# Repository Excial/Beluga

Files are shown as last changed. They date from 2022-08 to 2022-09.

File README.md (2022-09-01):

# Beluga
1. Created a sensor board for Beluga robotics platform
2. Contains PCB, Arduino Code

## Project description
A biosensor designed for microbial auditing, which is mounted onboard an autonomous robot as a payload. The PCB in this sensor helps to initiate helps to reduce the streamline the electronics due to space constraints to initiate the sampling sequence / processes of the biosensor.

## Design Objectives
Practice Design objectives in accordance to the IPC-2221 Standard

### V1
[✓] 3.3V LDO

[✓] 12V Buck Converter

[✓] ESP32 Module 

[✓] Bootloader

[✓] Troubleshooting LEDs

[X] Motor Driver LEDs

  - Too bright, need to increase resistance from 1K to 10K.

[✓] Motor Drivers

[X] Circuit Protection

  - Circuit Protection LED mounted wrongly, refer to schematic.
  - Source and Drain of Mosfet is mounted wrongly, needs to be switched.

[✓] M2 Mounting holes

#### Improvements
1. Add a stepper Motor driver
2. Add a buzzer
3. Add a USB Port
4. Add a FDTI chip
5. Increase Resistance for LEDs from 1k to 10K
	5a. Might Remove the LEDs altogether

### V2

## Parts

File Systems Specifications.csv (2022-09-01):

Name | id | Component_class | current | voltage | capacitance | inductance
ESP32 | C701342 | Microcontroller | 0.3A | 3.3V | - | - | -
A3909 | C2653462 | Motor Driver | 0.3A | 12V | - | - | SSOP-10
LED1,LED2,LED3 | C72043 | LED Diode | 0.02A | 3.3V | - | - | 0603
R81 | C14675 | Resistor | - | - | - | - | 0603
C3,C4,C5 | C92487 | Capacitor | - | 16V | 10uF | - | 0603
I1 | C2929502 | Inductor | 60V | 3A | - | 33uH | 12.3x12.3x3.8mm

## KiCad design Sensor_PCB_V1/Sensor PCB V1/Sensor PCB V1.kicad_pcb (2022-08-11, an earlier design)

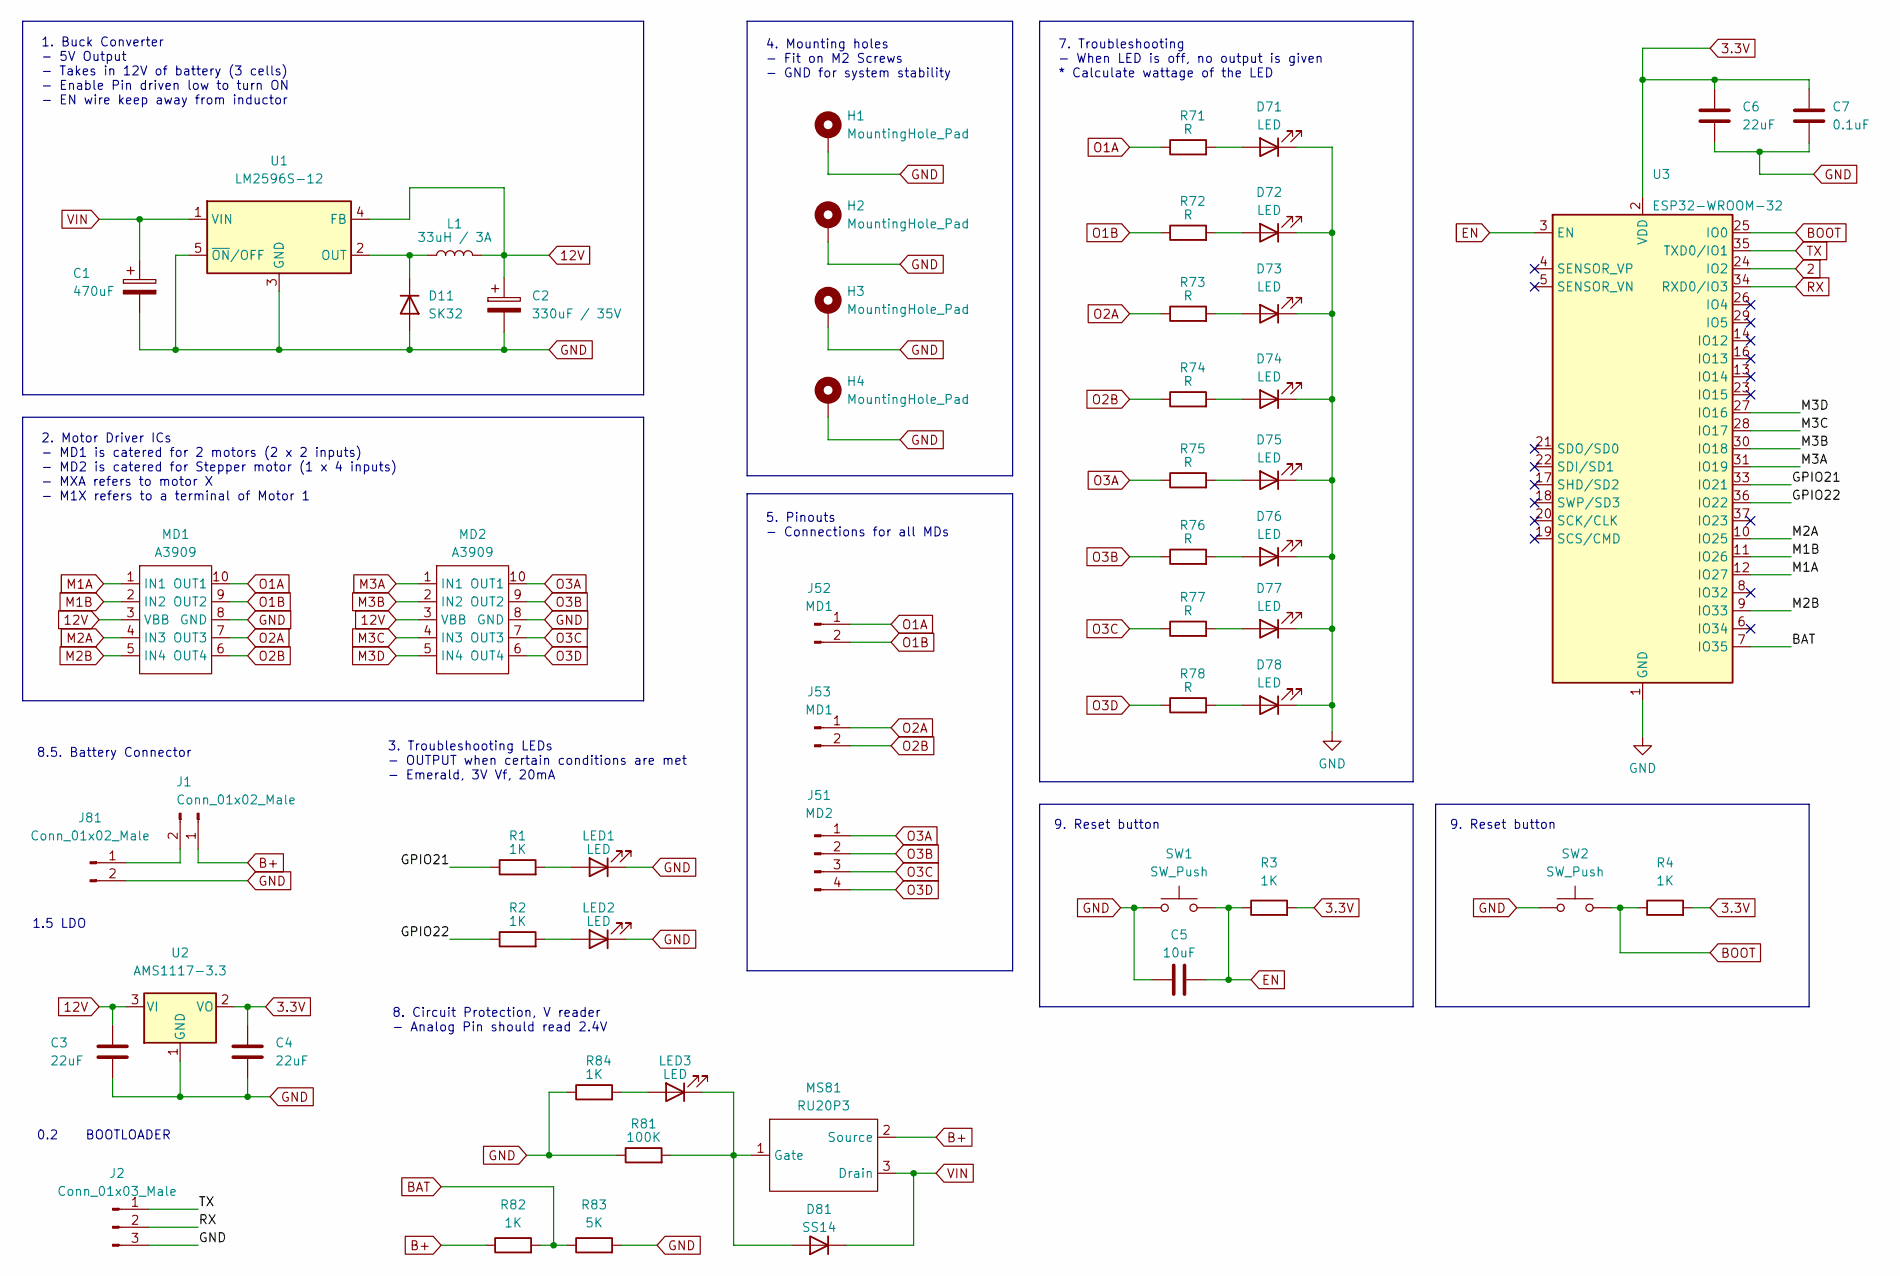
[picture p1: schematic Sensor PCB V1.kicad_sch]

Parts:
C1: 470uF; C_Elec_10x10.2
C2: 330uF / 35V; C_Elec_10x10.2
C3, C4, C6: 22uF; C_0603_1608Metric
C5: 10uF; C_0603_1608Metric
C7: 0.1uF; C_0603_1608Metric
D11: SK32; D_SOD-123F
D71, D72, D73, D74, D75, D76, D77, D78: LED; LED_0603_1608Metric
D81: SS14; D_SMA
H1, H2, H3, H4: MountingHole_Pad; MountingHole_2.2mm_M2_DIN965_Pad
J1, J81: Conn_01x02_Male; PinSocket_1x02_P2.54mm_Vertical
J2: Conn_01x03_Male; PinSocket_1x03_P2.54mm_Vertical
J51: MD2; PinSocket_1x04_P2.54mm_Vertical
J52, J53: MD1; PinSocket_1x02_P2.54mm_Vertical
L1: 33uH / 3A; L_12x12mm_H8mm
LED1, LED2, LED3: LED; LED_0603_1608Metric
MD1, MD2: A3909; SSOP-10_3.9x4.9mm_P1.00mm
MS81: RU20P3; SOT-23
R1, R2, R3, R4, R82, R84: 1K; R_0603_1608Metric
R71, R72, R73, R74, R75, R76, R77, R78: R; R_0603_1608Metric
R81: 100K; R_0603_1608Metric
R83: 5K; R_0603_1608Metric
SW1, SW2: SW_Push; SW_SPST_Omron_B3FS-100xP
U1: LM2596S-12; TO-263-5_TabPin3
U2: AMS1117-3.3; SOT-223-3_TabPin2
U3: ESP32-WROOM-32

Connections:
2: U3.24 (IO2)
3.3V: C4.1, C6.1, C7.1, R3.2, R4.2, U2.2 (VO), U3.2 (VDD)
12V: C2.1, C3.1, L1.2, MD1.3 (VBB), MD2.3 (VBB), U1.4 (FB), U2.3 (VI)
/GPIO21: R1.1, U3.33 (IO21)
/GPIO22: R2.1, U3.36 (IO22)
B+: J1.1, MS81.2 (Source), R82.1
BAT: R82.2, R83.1, U3.7 (IO35)
BOOT: R4.1, SW2.2, U3.25 (IO0)
EN: C5.2, R3.1, SW1.2, U3.3 (EN)
GND: C1.2, C2.2, C3.2, C4.2, C5.1, C6.2, C7.2, D11.2 (A), D71.1 (K), D72.1 (K), D73.1 (K), D74.1 (K), D75.1 (K), D76.1 (K), D77.1 (K), D78.1 (K), H1.1, H2.1, H3.1, H4.1, J2.3, J81.2, LED1.1 (K), LED2.1 (K), MD1.8 (GND), MD2.8 (GND), R81.1, R83.2, R84.1, SW1.1, SW2.1, U1.3 (GND), U1.5 (~ON/OFF), U2.1 (GND), U3.1 (GND), U3.15 (GND), U3.38 (GND), U3.39 (GND)
M1A: MD1.1 (IN1), U3.12 (IO27)
M1B: MD1.2 (IN2), U3.11 (IO26)
M2A: MD1.4 (IN3), U3.10 (IO25)
M2B: MD1.5 (IN4), U3.9 (IO33)
M3A: MD2.1 (IN1), U3.31 (IO19)
M3B: MD2.2 (IN2), U3.30 (IO18)
M3C: MD2.4 (IN3), U3.28 (IO17)
M3D: MD2.5 (IN4), U3.27 (IO16)
unnamed: D11.1 (K), L1.1, U1.2 (OUT)
unnamed: D71.2 (A), R71.2
unnamed: D72.2 (A), R72.2
unnamed: D73.2 (A), R73.2
unnamed: D74.2 (A), R74.2
unnamed: D75.2 (A), R75.2
unnamed: D76.2 (A), R76.2
unnamed: D77.2 (A), R77.2
unnamed: D78.2 (A), R78.2
unnamed: D81.2 (A), LED3.1 (K), MS81.1 (Gate), R81.2
unnamed: J1.2, J81.1
unnamed: LED1.2 (A), R1.2
unnamed: LED2.2 (A), R2.2
unnamed: LED3.2 (A), R84.2
O1A: J52.1, MD1.10 (OUT1), R71.1
O1B: J52.2, MD1.9 (OUT2), R72.1
O2A: J53.1, MD1.7 (OUT3), R73.1
O2B: J53.2, MD1.6 (OUT4), R74.1
O3A: J51.1, MD2.10 (OUT1), R75.1
O3B: J51.2, MD2.9 (OUT2), R76.1
O3C: J51.3, MD2.7 (OUT3), R77.1
O3D: J51.4, MD2.6 (OUT4), R78.1
RX: J2.2, U3.34 (RXD0/IO3)
TX: J2.1, U3.35 (TXD0/IO1)
VIN: C1.1, D81.1 (K), MS81.3 (Drain), U1.1 (VIN)

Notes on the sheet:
9. Reset button
8. Circuit Protection, V reader - Analog Pin should read 2.4V
3. Troubleshooting LEDs - OUTPUT when certain conditions are met - Emerald, 3V Vf, 20mA
1. Buck Converter - 5V Output - Takes in 12V of battery (3 cells) - Enable Pin driven low to turn ON - EN wire keep away from inductor
1.5 LDO
7. Troubleshooting - When LED is off, no output is given * Calculate wattage of the LED
5. Pinouts - Connections for all MDs
2. Motor Driver ICs - MD1 is catered for 2 motors (2 x 2 inputs) - MD2 is catered for Stepper motor (1 x 4 inputs) - MXA refers to motor X - M1X refers to a terminal of Motor 1
8.5. Battery Connector
4. Mounting holes - Fit on M2 Screws - GND for system stability
0.2 BOOTLOADER

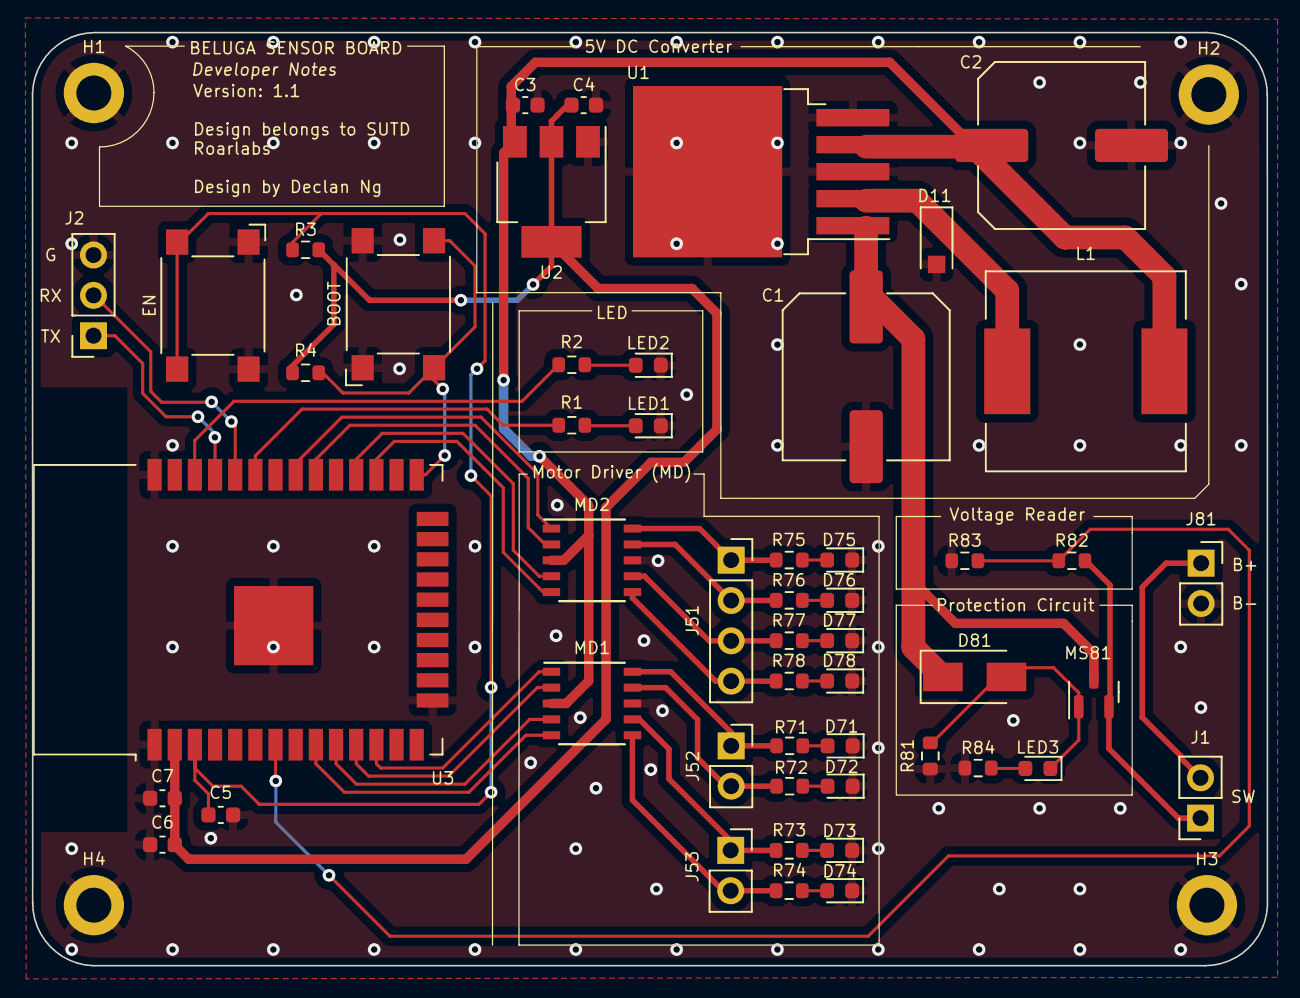
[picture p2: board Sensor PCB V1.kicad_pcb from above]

Board: 2 copper layers, 77.8 x 58.8 mm, 55 parts (0 on the bottom side), 42 nets.

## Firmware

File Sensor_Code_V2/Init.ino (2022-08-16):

void initSerial() {
  
  Serial.begin(9600);
  Serial.println("SERIAL OK");
  
}

void initSensor() {
  
  pinMode(sw1, INPUT); // Default logic is 0
  pinMode(sw2, INPUT); // Default logic is 0
  pinMode(m1, OUTPUT);
  pinMode(m2, OUTPUT);
  pinMode(m3, OUTPUT); // Naturally low (ie HIGH = COM and NC)
  pinMode(m4, OUTPUT); // Naturally low (ie HIGH = COM and NC)
  
}

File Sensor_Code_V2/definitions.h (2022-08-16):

// Pin definitions 
const int sw1 = 6; //Pin for switch 1 (Right side), Receive input from switch 1.
const int sw2 = 9; //Pin for switch 2 (Left side), Receive input from switch 2
const int m1 = 2; //Pin for Motor driver, Give output to motor driver 
const int m2 = 3; //Pin for Motor driver, Give output to motor driver 
const int m3 = 4; //Pin for Pump, Give output to Pump
const int m4 = 5; //Pin for Pump, Give output to Pump 

// State definitions
bool count = true; 
int times = 1;

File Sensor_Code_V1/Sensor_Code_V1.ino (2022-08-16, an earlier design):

const int sw1 = 6; //Pin for switch 1 (Right side), Receive input from switch 1.
const int sw2 = 9; //Pin for switch 2 (Left side), Receive input from switch 2
const int m1 = 2; //Pin for Motor driver, Give output to motor driver 
const int m2 = 3; //Pin for Motor driver, Give output to motor driver 
const int m3 = 4; //Pin for Pump, Give output to Pump
const int m4 = 5; //Pin for Pump, Give output to Pump 
bool count = true; 
int times = 1;

void setup() { 
  
  Serial.begin(9600);
  pinMode(sw1,INPUT); // Default logic is 0
  pinMode(sw2,INPUT); // Default logic is 0
  pinMode(m1,OUTPUT); 
  pinMode(m2,OUTPUT);
  pinMode(m3,OUTPUT); // Naturally low (ie HIGH = COM and NC)
  pinMode(m4,OUTPUT); // Naturally low (ie HIGH = COM and NC)
  //digitalWrite(m3, LOW); // Put it to HIGH to off first (ie be in NO mode), m3 = LOW and m4 = HIGH pumps clockwise 
  //digitalWrite(m4, HIGH); // Run once to have reagent reach the tip
  //delay(2250); // 5ml in 25 seconds; 1ml in 5 seconds; 50ul = 0.05ml required; max of 100ul = 0.1ml; Height should be 5.5cm
  //digitalWrite(m3, HIGH); // Either both HIGH or both LOW to ensure no motion
  delay(2000);
}

void moveLeft() {

  digitalWrite(m1,HIGH); // Move left and sensor is aligned
  digitalWrite(m2,LOW); 
  
}

void moveRight() {

  digitalWrite(m1,LOW); // Move right and pump is aligned
  digitalWrite(m2,HIGH); 
  
}

void stopMoving() {
  
  digitalWrite(m1,HIGH); // Pause motion
  digitalWrite(m2,HIGH);
  Serial.println("I have stopped");
  
}

void loop(){
  
  int out1 = digitalRead(sw1); // Print output of sw1 logic
  Serial.print("OUT1: ");
  Serial.println(out1);
  
  int out2 = digitalRead(sw2); // Print output of sw2 logic
  Serial.print("OUT2: ");
  Serial.println(out2);

  if(out1 == 1 && count == true && times == 1) {
      moveLeft();
      Serial.println("Start, I am moving left 1st time");
      Serial.println(times);
  }
  
  else if(out2 == 1 && count == true && times == 1) { // At left side 1st time (Sensor takes reading 1st time)
      stopMoving();
      count = false;
      Serial.println("I have reached far left 1st time");
      Serial.println(times);
      delay(60000);  
  }

  else if(out2 == 1 && count == false && times == 1) { // Move right 1st time 
      moveRight();
      Serial.println("I am moving right 1st time");
      Serial.println(times);
  }

  else if(out1 == 1 && count == false && times == 1){ // At right side 1st time (Pump takes reading)
      stopMoving();
      count = true;
      times += 1;
      Serial.println("I have reached far right 1st time");
      Serial.println(times);
      delay(2000);
      digitalWrite(m3, LOW);
      digitalWrite(m4, HIGH); 
      delay(500); // 5ml in 25 seconds; 1ml in 5 seconds; 50ul = 0.05ml required; max of 100ul = 0.1ml; Height should be 5.5cm
      digitalWrite(m3, HIGH);
      Serial.println("I have finished dispensing");
      delay(2000);
  }

  else if(out1 == 1 && count == true && times == 2){ // Move left 2nd time
      moveLeft();
      Serial.println("I am moving left 2nd time");
      Serial.println(times);
      
  }

  else if(out2 == 1 && count == true && times == 2){ // At left side 2nd time (Sensor takes reading 2nd time)
      stopMoving();
      count = false;
      Serial.println("I have reached far left 2nd time");
      Serial.println(times);
      delay(60000);
  }

  else if(out2 == 1 && count == false && times == 2) { // Move right 2nd time 
      moveRight();
      Serial.println("I am moving right 2nd time");
      Serial.println(times);
  }

  else if(out1 == 1 && count == false && times == 2){ // At right side 2nd time (End position)
      stopMoving();
      count = true;
      // times -= 1; // Uncomment this if want to loop
      times += 1; // To make sure system stop for good
      Serial.println("I have reached far right 2nd time, Finished");
      Serial.println(times);
      delay(2000);
      Serial.println("System will stop");
  }
  
}

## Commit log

2022-08-11 Completed V1
    [ESP32_Main.kicad_sch, Sensor PCB V1-all-pos.csv, Sensor PCB V1.csv, Sensor PCB V1.kicad_pcb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]
2022-08-16 Renamed a folder
    [ESP32_Main.kicad_sch, Sensor PCB V1-all-pos.csv, Sensor PCB V1.csv, Sensor PCB V1.kicad_pcb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]
2022-09-01 Added new folder for version 2
    [Sensor_Board_V2.kicad_pcb, Sensor_Board_V2.kicad_sch, Systems Specifications.csv]
